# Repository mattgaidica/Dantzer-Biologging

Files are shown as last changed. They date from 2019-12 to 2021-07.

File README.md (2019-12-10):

# What is bio-logging?
The use of miniaturized, animal-borne bio-loggers to make physiological and environmental measurements from free-ranging animals is radically transforming scientific capabilities ([Williams et al., 2019](https://besjournals.onlinelibrary.wiley.com/doi/abs/10.1111/1365-2656.13094)). We have recently explored how to implement these technologies to expand the methods and resolution by which stress and performance are quantified in the wild ([Gaidica & Dantzer, 2019](https://ecoevorxiv.org/huxw6/)).

### Current Challenges
Bio-logging is historically niche due to the unique constraints of field biologists. From fish to birds, it is unreasonable to expect a one-size-fits-all solution. However, the ambitious goals of individuals *can and should* generalize to the bio-logging community under the following headings:

1. _Standardize_ data collection and analysis methods.
2. _Communicate_ approaches and insights.
3. _Innovate_ tools and technologies.

We are doing our best to make our projects **open source**. You can read more about our approach in [the Wiki](https://github.com/mattgaidica/biologging/wiki/Architecture).

## Why squirrels?
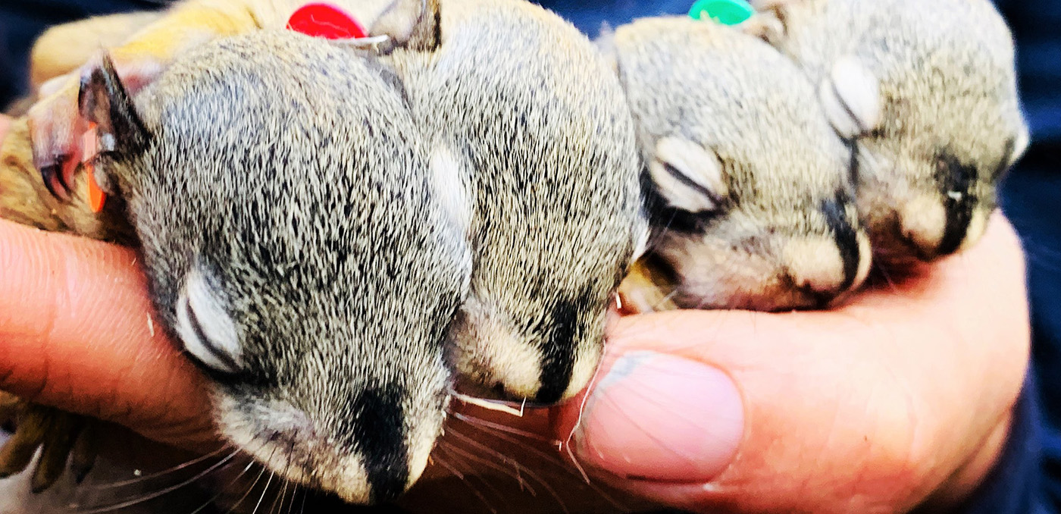
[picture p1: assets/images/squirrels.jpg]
squirrels

The ecological niche occupied by wild squirrels has been conserved for millions of years and is highlighted by their unique adaptations to arboreal life (i.e., in the trees). Their ability to regulate energy and maintain fitness through a variety of natural and imposed challenges ultimately determine their pedigree and survival. Little is known about how the central nervous system (CNS) is involved in these natural behaviors. One of our goals is to use bio-loggers to record from the CNS of wild squirrels to understand how their physiology and behavior are correlated, given the varying demands of their environment. Adding resolution to these important ecological factors is an important consideration to ongoing conservation work, potentially highlighting what ‘optimal adaptations’ are from a physiological perspective.

### Research Platform
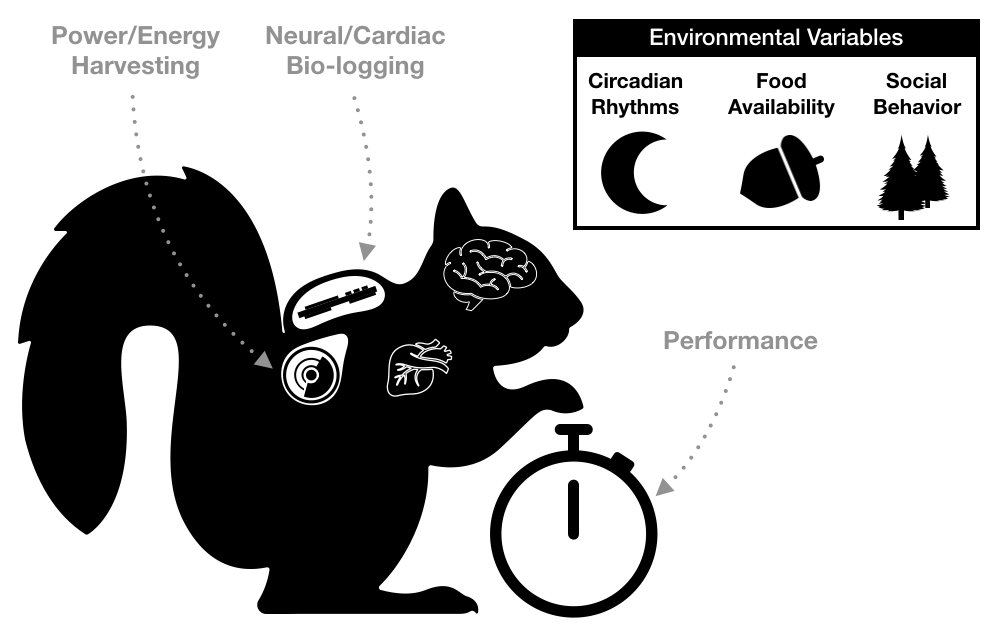
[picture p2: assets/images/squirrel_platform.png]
squirrel platform

Evolutionary pressures on wild animals engender advantageous platforms for study because behavior is so crucially linked with fitness. How mammalian physiology copes and adapts in response to changing environments is an important question that can benefit from the added resolution of bio-loggers. In addition to scientific investigations, the squirrel is a useful model to address many outstanding technical challenges—not unique to ecology—that make long-duration studies in harsh environments possible.

### Kluane Red Squirrel Project
[The Kluane Red Squirrel Project](https://redsquirrel.biology.ualberta.ca) (KRSP) is an interdisciplinary, large-scale field experiment located in the Canadian Yukon. KRSP has been collecting ecological and behavioral data on squirrels since 1987 and conducts a variety of studies and surveys on the population and food availability every year.

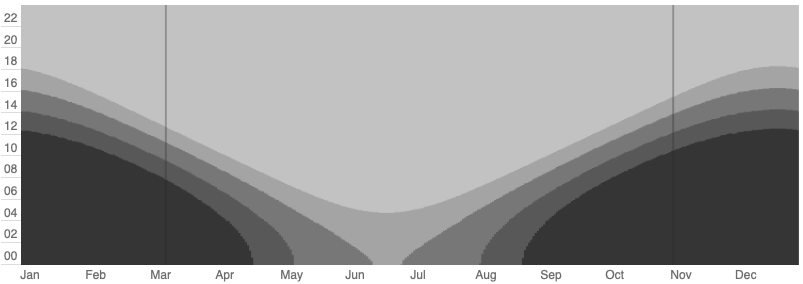
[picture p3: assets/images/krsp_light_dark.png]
whitehorse weather


Squirrels in the Yukon face intense challenges including drastic changes in light/dark cycles through each season. During the summer months there is very little darkness (see image above). This natural rhythm makes KRSP and the squirrel an ideal candidate to study the affects of circadian entrainment.

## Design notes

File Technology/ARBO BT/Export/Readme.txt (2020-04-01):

FR4, 1.6mm (0.062") thickness
1oz weight (or default/standard for copper)
Soldermask two-sided preferred, but whatever is cheapest, don't need both
4 layers
1.6mm thickness
.076mm (3mil) min trace
0.45/0.2mm through via
0.28/0.15mm blind/buried via

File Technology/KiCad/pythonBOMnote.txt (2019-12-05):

/Applications/KiCad/kicad.app/Contents/Frameworks/Python.framework/Versions/Current/bin/python "/Users/matt/Box Sync/Biologging/Technology/KiCad/KiBoM/KiBOM_CLI.py" "%I" "%O"

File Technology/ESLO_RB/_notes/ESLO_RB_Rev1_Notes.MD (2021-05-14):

SysConfig
-
* Disable DCDC (I think it does this automatically)
* Remove Axy_CS
* Change EEG_SPI to input when not used
* Remove pull-up from I2C pin instances

__Optimization__
* Build > Arm Compiler > Optimization [Optimization level -> turn on], [Floating point mode -> relaxed] will result in faster execution but may decrease precision

Hardware
-
Although you say your design seems to be operational, I’d still recommend following the CC2652RB reference design regarding the VDDS and VDDR decoupling capacitors to avoid performance issues with the RF. I also noticed that you’re missing the DCDC_SW 6.8uH inductor (L1 in the reference design). This is critical for suppressing the Switching Noise from the DC-DC Converter.

Here are some helpful links:

* SimpleLink Crystal-less BAW CC2652RB multiprotocol 2.4GHz wireless MCU dev kit (Rev. A) 
* CC13xx/CC26xx Hardware Configuration and PCB Design Considerations (Rev. E)

Alexis Rodriguez, a.rodriguez@ti.com

Additions
-
* Add UART debugging pins/test points (2 pins, RX&TX)
* Better SPI probe points for debugging

Fixes
-
__CMSIS__

* This post is not relevant, seems to be for old versions of CMSIS [E2E Forums](https://e2e.ti.com/support/microcontrollers/other/f/908/t/640978?CCS-Issues-Setting-Up-CMSIS-DSP-in-CCS#pi320995=2)
* Post on [Benchmarking FFTs](http://openaudio.blogspot.com/2016/09/benchmarking-fft-speed.html)
* [CMSIS Docs](https://docs.silabs.com/cmsis/latest/dsp/group-RealFFT#ga180d8b764d59cbb85d37a2d5f7cd9799)

1. Download CMSIS .pack from Github
2. Unpack using >> unpack200 -r -v "/Users/matt/Downloads/CMSIS.pack" "/Users/matt/Downloads/CMSIS.jar"
3. Extract .jar using The Unarchiver
4. Create static library in CCS: New project, import math files, add Include to path. *Some includes need to be copied/pasted into DSP Include (from Private Include and Core Include)*
5. Build project, link to .lib file in Debug folder from other projects.

Est. ~0.26ms for init, FFT, and findMaxBin. See also: [TI debug counter/time in CCS](http://downloads.ti.com/ccs/esd/training/workshop/ccsv7/cc13x0/site/#counter)
* Use atan2() to get angle from complex result: https://stackoverflow.com/questions/16601252/c-equivalent-of-matlab-angle-function and http://gaidi.ca/weblog/forecasting-slow-wave-activity-from-eeg-using-fft

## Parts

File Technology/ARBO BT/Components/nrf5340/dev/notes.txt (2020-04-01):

Set env variables:
>> cd /Users/matt/Documents/Software/ncs/zephyr
>> source zephyr-env.sh

>> west build -b nrf5340_dk_nrf5340_cpuapp

try setting board default?
>> west config build.board nrf5340_dk_nrf5340_cpuapp

Pristine builds:
>> west build -p auto -b nrf5340_dk_nrf5340_cpuapp samples/hello_world

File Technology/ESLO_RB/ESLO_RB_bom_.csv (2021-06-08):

Component | Description | Part | References | Value | Footprint | Quantity Per PCB | Datasheet | Digikey | Mouser
1 | Antenna | Antenna | AE1 | 2450AT42B100 | 2450AT42B100 | 1 | ~ | 712-1008-1-ND‎
2 | Unpolarized capacitor | C | C3 C11 C15 C17 C20 C22 C23 C25 C26 C27 C28 C29 | 0.1uF | C_0402_1005Metric | 12 | ~ | 490-6328-1-ND
3 | Unpolarized capacitor | C | C7 | 0.22uF | C_0402_1005Metric | 1 | ~ | 1276-1176-1-ND
4 | Unpolarized capacitor | C | C10 | 10nF | C_0402_1005Metric | 1 | ~ | 1276-1051-1-ND
5 | Unpolarized capacitor | C | C1 C2 C4 C6 | 10uF | C_0603_1608Metric | 4 | ~ | 490-14372-1-ND
6 | Unpolarized capacitor | C | C19 | 1nF | C_0402_1005Metric | 1 | ~ | 478-1101-1-ND
7 | Unpolarized capacitor | C | C5 C9 C14 C16 C18 C21 C24 | 1uF | C_0402_1005Metric | 7 | ~ | 399-4873-1-ND
8 | Unpolarized capacitor | C | C8 C12 | 2.2uF | C_0402_1005Metric | 2 | ~ | 1276-1469-1-ND
9 | Unpolarized capacitor | C | C13 | 22uF | C_0603_1608Metric | 1 | ~ | 1276-2867-1-ND
10 | 4 capacitor network, parallel topology, DIP package | C_Pack04 | CN2 CN3 | 1000pF | 0508_array | 2 | ~ | 478-W2A45C102KAT2ACT-ND
11 | 4 capacitor network, parallel topology, DIP package | C_Pack04 | CN4 CN5 | 1uF | 0508_array | 2 | ~ |  | 581-W2L16D105MAT1A
12 | 4 capacitor network, parallel topology, DIP package | C_Pack04 | CN1 | 4700pF | 0508_array | 1 | ~ |  | 581-W2A41C472KAT2A
13 | Light emitting diode | LED | D1 | LED | LED_0603_1608Metric | 1 | ~ | SML-D12V1WT86CT-ND
14 | Generic connector, single row, 01x10, script generated (kicad-library-utils/schlib/autogen/connector/) | Conn_01x10_Female | J1 | 10POS Biopotentials | ARBO_IO10_1.27mm | 1 | ~ | ED10276-ND
15 | Generic connector, single row, 01x06, script generated (kicad-library-utils/schlib/autogen/connector/) | Conn_01x06_Female | J2 | 6POS Power/JTAG | ARBO_IO6_1.27mm | 1 | ~ | ED10273-ND
16 | Inductor | L | L3 | 1.5nH | L_0402_1005Metric | 1 | ~ | 712-1411-1-ND
17 | Inductor | L | L1 | 2.2uH | L_0805_2012Metric | 1 | ~ | 490-7781-1-ND
18 | Inductor | L | L4 | 3.3nH | L_0402_1005Metric | 1 | ~ | 712-1416-1-ND
19 | Inductor | L | L2 | BLM18HE152SN1 | L_0603_1608Metric | 1 | ~ | 490-5216-1-ND
20 | Net tie, 2 pins | Net-Tie_2 | NT1 | Net-Tie_2 | NetTie-2_SMD_Pad0.5mm | 1 | ~
21 | Resistor | R | R1 R2 R3 R8 | 100k | LED_0402_1005Metric | 4 | ~ | 311-100KLRCT-ND
22 | Resistor | R | R4 | 21.5k | R_0402_1005Metric | 1 | ~ | RMCF0402FT21K5CT-ND
23 | Resistor | R | R6 R7 | 4.7k | R_0402_1005Metric | 2 | ~ | 311-4.7KJRCT-ND
24 | Resistor | R | R5 | 80.6k | R_0402_1005Metric | 1 | ~ | RMCF0402FT80K6CT-ND
25 | 4 resistor network, parallel topology, DIP package | R_Pack04 | RN3 RN4 | 1M | 0502_array | 2 | ~ | Y6105CT-ND
26 | 4 resistor network, parallel topology, DIP package | R_Pack04 | RN1 RN2 | 4.7k | 0502_array | 2 | ~ | Y6472CT-ND
27 |  | 2450BM14G0011 | U10 | 2450BM14G0011 | 2450BM14G0011 | 1 |  | 712-1620-1-ND
28 |  | ADS1294 | U9 | ADS1294 | BGA-64_8x8_8.0x8.0mm_ADS129x | 1 |  | 296-28024-1-ND
29 |  | CC2652RB | U8 | CC2652RB | QFN-48-1EP_7x7mm_P0.5mm_EP5.15x5.15mm | 1 |  | 296-CC2652RB1FRGZRCT-ND
30 | FRAM memory with SPI interface, SOIC-8 SON-8 | MB85RS2MT | U3 | CY15V104QI-20LPXC | 8-GQFN_FRAM_3.28mm-3.23mm | 1 | http://www.fujitsu.com/downloads/MICRO/fsa/pdf/products/memory/fram/MB85RS16-DS501-00014-6v0-E.pdf | 428-4724-ND
31 | 250-mA Ultra-Low-Noise Low-IQ LDO, 1.8V, SOT-23 | LP5907MFX-1.8 | U5 | LP5907MFX-1.5 | SOT-23-5 | 1 | http://www.ti.com/lit/ds/symlink/lp5907.pdf | 296-40355-1-ND
32 |  | LSM303AGR | U4 | LSM303AGR | LGA-12_2x2mm_P0.5mm | 1 |  | 497-16527-1-ND
33 |  | MAX1720 | U1 | MAX1720 | SOT-23-6 | 1 |  | MAX1720EUTGOSCT-ND
34 |  | IS37SML01G1 | U7 | MT29F2G01ABBGDWB-IT:G TR | 8x6mm_WSON_UTSO | 1 |  | 557-1665-1-ND
35 |  | TPS62740 | U2 | TPS62740 | WSON-12-1EP_3x2mm_P0.5mm_EP1x2.65 | 1 |  | 296-39459-1-ND
36 |  | TPS72325 | U6 | TPS72301DDCT | SOT-23-5 | 1 |  | 296-38438-1-ND
Component Groups: | 36
Component Count: | 65
Fitted Components: | 65
Number of PCBs: | 1
Total components: | 65
Schematic Version:
Schematic Date:
BoM Date: | Friday, June 04, 2021 at 01:24:00 PM
Schematic Source: | /Users/matt/Box Sync/Biologging/Technology/ESLO_RB/ESLO_RB.sch
KiCad Version: | Eeschema (5.1.5-0-10_14)

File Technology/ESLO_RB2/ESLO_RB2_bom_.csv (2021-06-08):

Component | Description | Part | References | Value | Footprint | Quantity Per PCB | Datasheet | Digikey | Mouser
1 | Antenna | Antenna | AE1 | 2450AT42B100 | 2450AT42B100 | 1 | ~ | 712-1008-1-ND‎
2 | Unpolarized capacitor | C | C11 C15 C17 C20 C22 C23 C25 C26 C27 C28 C29 | 0.1uF | C_0402_1005Metric | 11 | ~ | 490-6328-1-ND
3 | Unpolarized capacitor | C | C10 | 10nF | C_0402_1005Metric | 1 | ~ | 1276-1051-1-ND
4 | Unpolarized capacitor | C | C1 C2 C4 | 10uF | C_0603_1608Metric | 3 | ~ | 478-10766-2-ND
5 | Unpolarized capacitor | C | C30 C31 | 12pF | C_0402_1005Metric | 2 | ~ | 490-5924-2-ND
6 | Unpolarized capacitor | C | C19 | 1nF | C_0402_1005Metric | 1 | ~ | 478-1101-1-ND
7 | Unpolarized capacitor | C | C3 C5 C14 C16 C18 C24 | 1uF | C_0402_1005Metric | 6 | ~ | 399-4873-1-ND
8 | Unpolarized capacitor | C | C21 | 1uF | C_0603_1608Metric | 1 | ~ | 399-7847-2-ND
9 | Unpolarized capacitor | C | C7 C12 | 2.2uF | C_0402_1005Metric | 2 | ~ | 1276-1781-2-ND
10 | Unpolarized capacitor | C | C13 | 22uF | C_0603_1608Metric | 1 | ~ | 1276-1193-2-ND
11 | Unpolarized capacitor | C | C6 | 4.7uF | C_0402_1005Metric | 1 | ~ | 1276-1484-2-ND
12 | 4 capacitor network, parallel topology, DIP package | C_Pack04 | CN4 CN5 | 0.1uF | 0508_array | 2 | ~ | 478-7584-2-ND
13 | 4 capacitor network, parallel topology, DIP package | C_Pack04 | CN2 CN3 | 1000pF | 0508_array | 2 | ~ | 478-13177-2-ND
14 | 4 capacitor network, parallel topology, DIP package | C_Pack04 | CN1 | 4700pF | 0612_array | 1 | ~ | 399-CA064X473K4RACTUTR-ND
15 | Light emitting diode | LED | D1 D2 | LED | LED_0402_1005Metric | 2 | ~ | VLMB1500-GS08CT-ND VLMO1500-GS08CT-ND
16 | Ferrite bead | Ferrite_Bead | FB1 | Ferrite_Bead | C_0603_1608Metric | 1 | ~ | 490-5216-2-ND
17 | Generic connector, single row, 01x08, script generated (kicad-library-utils/schlib/autogen/connector/) | Conn_01x08_Female | J1 J2 | Biopotentials | ESLO_IO_8_1-27 | 2 | ~ | ED8250-ND ED90570-ND
18 | Generic connector, single row, 01x02, script generated (kicad-library-utils/schlib/autogen/connector/) | Conn_01x02_Female | J3 | Conn_01x02_Female | ESLO_2pin_THERM | 1 | ~
19 | Inductor | L | L3 | 1.5nH | L_0402_1005Metric | 1 | ~ | 334-1083-2-ND
20 | Inductor | L | L1 | 2.2uH | L_0805_2012Metric | 1 | ~ | 490-4994-2-ND
21 | Inductor | L | L4 | 3.3nH | L_0402_1005Metric | 1 | ~ | 712-1416-1-ND
22 | Net tie, 2 pins | Net-Tie_2 | NT1 | Net-Tie_2 | NetTie-2_SMD_Pad0.5mm | 1 | ~
23 | Resistor | R | R1 R2 R3 R8 | 100k | LED_0402_1005Metric | 4 | ~ | 311-100KLRCT-ND
24 | Resistor | R | R4 | 21.5k | R_0402_1005Metric | 1 | ~ | RMCF0402FT21K5CT-ND
25 | Resistor | R | R5 | 80.6k | R_0402_1005Metric | 1 | ~ | RMCF0402FT80K6CT-ND
26 | 4 resistor network, parallel topology, DIP package | R_Pack04 | RN3 RN4 | 1M | 0502_array | 2 | ~ | Y6105CT-ND
27 | 4 resistor network, parallel topology, DIP package | R_Pack04 | RN1 RN2 | 4.7k | 0502_array | 2 | ~ | Y6472CT-ND
28 |  | 2450BM14G0011 | U10 | 2450BM14G0011 | 2450BM14G0011 | 1 |  | 712-1620-1-ND
29 |  | ADS1294 | U9 | ADS1294 | BGA-64_8x8_8.0x8.0mm_ADS129x | 1 |  | 296-28024-1-ND
30 |  | IS37SML01G1 | U7 | AS5F18G04SND-10LIN | 8x6mm_WSON_UTSO | 1 |  | 1450-AS5F18G04SND-10LIN-ND | 340-319932-REEL
31 |  | CC2652RB | U8 | CC2652R1FRGZT | QFN-48-1EP_7x7mm_P0.5mm_EP5.15x5.15mm | 1 |  |  | 595-CC2652R1FRGZR
32 | I2C/SPI, iNEMO inertial module: always-on 3D accelerometer and 3D gyroscope | LSM6DS3 | U3 | LSM6DSOXTR | LGA-14_3x2.5mm_P0.5mm_LayoutBorder3x4y | 1 | www.st.com/resource/en/datasheet/lsm6ds3.pdf | 497-18367-2-ND
33 |  | MAX1720 | U1 | MAX1720 | SOT-23-6 | 1 |  | MAX1720EUTGOSCT-ND
34 |  | TPS62243_WSON | U4 | TPS62243_WSON | WSON-6-1EP_2x2mm_P0.65mm_EP1x1.6mm | 1 |  | 296-46476-1-ND
35 |  | TPS723_WSON | U6 | TPS72301DRVR | WSON-6-1EP_2x2mm_P0.65mm_EP1x1.6mm | 1 |  | 296-TPS72301DRVRTR-ND
36 |  | TPS7A20_X2SON | U2 | TPS7A2015PDQNR | Texas_X2SON-4_1x1mm_P0.65mm | 1 |  | 296-TPS7A2015PDQNRTR-ND
37 | Two pin crystal | Crystal | Y2 | 32.768kHz | Crystal_SMD_2012-2Pin_2.0x1.2mm | 1 | ~ | SER4081TR-ND
38 | Four pin crystal, GND on pins 2 and 4 | Crystal_GND24 | Y1 | 48MHz | Crystal_SMD_2016-4Pin_2.0x1.6mm | 1 | ~ | 535-13927-2-ND
Component Groups: | 38
Component Count: | 66
Fitted Components: | 66
Number of PCBs: | 1
Total components: | 66
Schematic Version:
Schematic Date:
BoM Date: | Tuesday, June 01, 2021 at 11:29:35 AM
Schematic Source: | /Users/matt/Box Sync/Biologging/Technology/ESLO_RB2/ESLO_RB2.sch
KiCad Version: | Eeschema (5.1.5-0-10_14)

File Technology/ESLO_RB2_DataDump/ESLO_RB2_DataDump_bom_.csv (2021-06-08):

Component | Description | Part | References | Value | Footprint | Quantity Per PCB | Datasheet | Digikey
1 | Unpolarized capacitor | C | C2 | 10uF | C_0603_1608Metric | 1 | ~ | 478-8050-1-ND
2 | Generic connector, single row, 01x08, script generated (kicad-library-utils/schlib/autogen/connector/) | Conn_01x08_Female | J1 | Conn_01x08_Female | 8pin_1-27pitch_SMD | 1 | ~ | ED90570-ND
3 | Capacitor symbol for simulation only | INDUCTOR | L1 | 2.2uH | L_0805_2012Metric | 1 | ~ | 490-4994-1-ND
4 | Resistor | R | R1 R2 | 10k | R_0603_1608Metric | 2 | ~ | CR0603-JW-103ELFCT-ND
5 | Resistor | R | R3 R4 | 8.25k | R_0603_1608Metric | 2 | ~ | RMCF0603FT8K25CT-ND
6 | Double Pole Single Throw (DPST) Switch | SW_DPST | SW1 | SW_DPST | SW_SPST_TL3305A | 1 | ~ | EG5353CT-ND
7 |  | Adalogger | U2 | Adalogger | Adafruit_feather | 1 |  | 1528-1539-ND
8 |  | SN74ACX1T45 | U3 U4 | SN74ACX1T45 | SOT-363_SC-70-6 | 2 |  | 296-SN74AXC1T45QDCKRQ1CT-ND
9 |  | TPS62243_WSON | U1 | TPS62243_WSON | WSON-6-1EP_2x2mm_P0.65mm_EP1x1.6mm | 1 |  | TPS62243DRVR
Component Groups: | 9
Component Count: | 12
Fitted Components: | 12
Number of PCBs: | 1
Total components: | 12
Schematic Version:
Schematic Date:
BoM Date: | Wednesday, June 02, 2021 at 09:34:16 AM
Schematic Source: | /Users/matt/Box Sync/Biologging/Technology/ESLO_RB2_DataDump/ESLO_RB2_DataDump.sch
KiCad Version: | Eeschema (5.1.5-0-10_14)

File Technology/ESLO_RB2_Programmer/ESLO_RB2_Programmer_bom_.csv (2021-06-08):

Component | Description | Part | References | Value | Footprint | Quantity Per PCB | Datasheet | Digikey
1 | Unpolarized capacitor | C | C1 | 10uF | C_0603_1608Metric | 1 | ~ | 478-8050-1-ND‎
2 | Light emitting diode | LED | D1 | LED | D_0603_1608Metric | 1 | ~ | 475-3442-1-ND
3 | Generic connector, single row, 01x08, script generated (kicad-library-utils/schlib/autogen/connector/) | Conn_01x08_Female | J3 | Conn_01x08_Female | 8pin_1-27pitch_SMD | 1 | ~ | ED90570-ND
4 | Generic connector, single row, 01x03, script generated (kicad-library-utils/schlib/autogen/connector/) | Conn_01x03_Male | J1 | LP-P10 | PinHeader_1x03_P2.54mm_Vertical | 1 | conn-SAM8930-ND | A19430-ND
5 | Cortex Debug Connector, standard ARM Cortex-M SWD and JTAG interface | Conn_ARM_JTAG_SWD_10 | J2 | LP-P7 | PinHeader_2x05_P1.27mm_Vertical_SMD | 1 | http://infocenter.arm.com/help/topic/com.arm.doc.ddi0314h/DDI0314H_coresight_components_trm.pdf | SAM13165CT-ND
6 | Capacitor symbol for simulation only | INDUCTOR | L1 | 2.2uH | R_0805_2012Metric | 1 | ~ | 490-4994-1-ND‎
7 | Switch, single pole double throw | SW_SPDT | SW1 | SW_SPDT | PinSocket_1x03_P2.54mm_Vertical | 1 | ~ | 360-2133-ND
8 |  | TPS62243_WSON | U1 | TPS62243_WSON | WSON-6-1EP_2x2mm_P0.65mm_EP1x1.6mm | 1 |  | 296-46476-1-ND‎
Component Groups: | 8
Component Count: | 8
Fitted Components: | 8
Number of PCBs: | 1
Total components: | 8
Schematic Version:
Schematic Date:
BoM Date: | Wednesday, June 02, 2021 at 09:28:16 AM
Schematic Source: | /Users/matt/Box Sync/Biologging/Technology/ESLO_RB2_Programmer/ESLO_RB2_Programmer.sch
KiCad Version: | Eeschema (5.1.5-0-10_14)

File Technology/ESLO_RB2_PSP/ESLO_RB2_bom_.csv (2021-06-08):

Component | Description | Part | References | Value | Footprint | Quantity Per PCB | Datasheet | Digikey | Mouser
1 | Antenna | Antenna | AE1 | 2450AT42B100 | 2450AT42B100 | 1 | ~ | 712-1008-1-ND‎
2 | Unpolarized capacitor | C | C11 C17 C20 C22 C23 C25 C26 C28 C29 | 0.1uF | C_0402_1005Metric | 9 | ~ | 490-6328-1-ND
3 | Unpolarized capacitor | C | C10 | 10nF | C_0402_1005Metric | 1 | ~ | 1276-1051-1-ND
4 | Unpolarized capacitor | C | C2 C4 | 10uF | C_0603_1608Metric | 2 | ~ | 478-10766-2-ND
5 | Unpolarized capacitor | C | C30 C31 | 12pF | C_0402_1005Metric | 2 | ~ | 490-5924-2-ND
6 | Unpolarized capacitor | C | C3 C5 C21 | 1uF | C_0402_1005Metric | 3 | ~ | 399-4873-1-ND
7 | Unpolarized capacitor | C | C1 C12 | 2.2uF | C_0402_1005Metric | 2 | ~ | GRM155R61E225KE11D
8 | Unpolarized capacitor | C | C6 | 4.7uF | C_0402_1005Metric | 1 | ~ | 1276-1484-2-ND
9 | Light emitting diode | LED | D1 D2 | LED | LED_0603_1608Metric | 2 | ~ | SML-D12V1WT86CT-ND
10 | Generic connector, single row, 01x08, script generated (kicad-library-utils/schlib/autogen/connector/) | Conn_01x08_Female | J1 J2 | Biopotentials | ESLO_IO_8_1-27 | 2 | ~ | ED8250-ND ED90570-ND
11 | Generic connector, single row, 01x02, script generated (kicad-library-utils/schlib/autogen/connector/) | Conn_01x02_Female | J3 | Conn_01x02_Female | ESLO_2pin_THERM | 1 | ~
12 | Inductor | L | L3 | 1.5nH | L_0402_1005Metric | 1 | ~ | 334-1083-2-ND
13 | Inductor | L | L1 | 2.2uH | L_0805_2012Metric | 1 | ~ | 490-4994-2-ND
14 | Inductor | L | L4 | 3.3nH | L_0402_1005Metric | 1 | ~ | 712-1416-1-ND
15 | Net tie, 2 pins | Net-Tie_2 | NT1 | Net-Tie_2 | NetTie-2_SMD_Pad0.5mm | 1 | ~
16 | Resistor | R | R1 R2 R3 R8 | 100k | LED_0402_1005Metric | 4 | ~ | 311-100KLRCT-ND
17 | Resistor | R | R4 | 21.5k | R_0402_1005Metric | 1 | ~ | RMCF0402FT21K5CT-ND
18 | Resistor | R | R5 | 80.6k | R_0402_1005Metric | 1 | ~ | RMCF0402FT80K6CT-ND
19 |  | 2450BM14G0011 | U10 | 2450BM14G0011 | 2450BM14G0011 | 1 |  | 712-1620-1-ND
20 |  | IS37SML01G1 | U7 | AS5F18G04SND-10LIN | 8x6mm_WSON_UTSO | 1 |  | 1450-AS5F34G04SND-08LIN-ND | 340-319932-REEL
21 |  | CC2652RB | U8 | CC2652R1FRGZT | QFN-48-1EP_7x7mm_P0.5mm_EP5.15x5.15mm | 1 |  |  | 595-CC2652R1FRGZR
22 | I2C/SPI, iNEMO inertial module: always-on 3D accelerometer and 3D gyroscope | LSM6DS3 | U3 | LSM6DSOXTR | LGA-14_3x2.5mm_P0.5mm_LayoutBorder3x4y | 1 | www.st.com/resource/en/datasheet/lsm6ds3.pdf | 497-18367-2-ND
23 |  | MAX1720 | U1 | MAX1720 | SOT-23-6 | 1 |  | MAX1720EUTGOSCT-ND
24 |  | TPS6223xx | U4 | TPS6223xx | USON6-1.45x1.00mm-0.5pads | 1 |  | 296-39453-2-ND
25 |  | TPS72325 | U6 | TPS72301DRVR | WSON-6-1EP_2x2mm_P0.65mm_EP1x1.6mm | 1 |  | 296-TPS72301DRVRTR-ND
26 |  | TPS7A20_X2SON | U2 | TPS7A2015PDQNR | Texas_X2SON-4_1x1mm_P0.65mm | 1 |  | 296-TPS7A2015PDQNRTR-ND
27 | Two pin crystal | Crystal | Y2 | 32.768kHz | Crystal_SMD_2012-2Pin_2.0x1.2mm | 1 | ~ | SER4081TR-ND
28 | Four pin crystal, GND on pins 2 and 4 | Crystal_GND24 | Y1 | 48MHz | Crystal_SMD_2016-4Pin_2.0x1.6mm | 1 | ~ | 535-13927-2-ND
Component Groups: | 28
Component Count: | 46
Fitted Components: | 46
Number of PCBs: | 1
Total components: | 46
Schematic Version:
Schematic Date:
BoM Date: | Monday, May 03, 2021 at 05:46:10 PM
Schematic Source: | /Users/matt/Box Sync/Biologging/Technology/ESLO_RB2_PSP/ESLO_RB2.sch
KiCad Version: | Eeschema (5.1.5-0-10_14)

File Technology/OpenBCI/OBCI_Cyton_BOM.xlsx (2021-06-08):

 | OBCI_V3_C
Item | Board Ref | Qty | Component | Value | Package | Manufacturer | Part Number | Description | Notes
1 | C2,C4 | 2 | C | 100uF | SM 1206 | Yageo | CC1206MKX5R5BB107 | MLCC
2 | C1,C8,C25,C29,C31,C33,C37 | 7 | C | 10uF | SM0603 | Murata | GRM188C80G106KE47D | MLCC
3 | C32,C35,C36,C38,C40 | 5 | C | 2.2uF | EIA_0402 | Murata | GRM155C80J225ME95D | MLCC
4 | C39 | 1 | C | 2.2uF | EIA_0402 | Murata | GRM155R61C225KE44D | MLCC
5 | C6,C7,C14,C17,C18,C19,C21,C22,C27 | 9 | C | 1uF | EIA_0402 | Yageo | CC0402KRX7R5BB105 | MLCC
6 | C5,C10,C12,C13,C15,C24,C28 | 7 | C | 0.1uF | EIA_0402 | Yageo | CC0402KRX7R7BB104 | MLCC
7 | C30 | 1 | C | 0.01uF | EIA_0402 | Yageo | CC0402KRX7R7BB103 | MLCC
8 | C16 | 1 | C | 0.001uF | EIA_0402 | Yageo | CC0402KRX7R7BB102 | MLCC
9 | C20,C23 | 2 | C | 18pF | EIA_0402 | Yageo | CC0402JRNPO9BN180 | MLCC
10 | R1,R2,R3,R4,R6 | 5 | R | 2.2K | SM | BOURNS | CAY16-2201F4LF | 4 R-ARRAY
11 | C3,C9,C11,C26,C34 | 5 | C | 0.001uF | SM | TDK | CKCL44X7R1H102M085AA | 4 CAP ARRAY
12 | U1 | 1 | U |  | LGA | ST | LIS3DHTR | ST ACCELEROMETER
13 | U2 | 1 | U |  | SM | TI | SN74LVC1G32DCKR | OR_GATE
14 | U3 | 1 | U |  | SOT-23-6 | TI | LM2664M6/NOPB | V INVERTER
15 | U4 | 1 | U |  | SOT-23-5 | TI | TLV70025QDDCRQ1 | +2.5V LDO REG
16 | U5 | 1 | U |  | SM | Microchip | MCP1754T-3302E/OT | 3V3 LDO REG
17 | U6 | 1 | U |  | TQFP-64 | TI | ADS1299IPAG | ADS1299 | Consigned by OpenBCI, Inc
18 | U7 | 1 | U |  | SSOP-28 | Microchip | PIC32MX250F128B-I/SS | PIC32 MICROCONTROLLER
19 | VR1 | 1 | VR |  | SM | TI | TPS72325DBVR | -2.5 LDO REG
20 | BLE1 | 1 | BLE |  | SM | RF DIGITAL | RFD22301 | BTLE Module | Consigned by OpenBCI, Inc
21 | D1 | 1 | D | LED | SM 0603 | Lite-On | LTST-C193TBKT-5A | BLUE LED
22 | D8 | 2 | D |  | SM 0603 | Comchip | CDSU400B | DIODE
23 | D9 | 1 | D |  | SM 0603 | Comchip | CDBU0130L | DIODE
24 | D2,D3,D4,D5,D6,D7 | 6 | D |  | SM | TI | TPD4E1B06DCKR | TI QUAD TVS
25 | D10 | 1 | D | 3V | SOD-923 | Comchip | CZRQR52C3-HF | 3V Zener Diode
26 | R8,R10,R11 | 3 | R | 1K | EIA_0402 | Yageo | RT0402FRE071KL | Resistor
27 | R5 | 1 | R | 1M | EIA_0402 | Yageo | RC0402JR-071ML | Resistor
28 | R7,R9 | 2 | R | 470K | EIA_0402 | Yageo | RC0402JR-07470KL | Resistor
29 | X1 | 1 | X | 8MHz | SM | ABRACON | ABMM2-8.000MHZ-E2-T | 8MHz XTAL
30 | B1 | 1 | BATT |  | SM | JST Sales | S2B-PH-SM4-TB(LF)(SN) | CONN HEADER PH SIDE 2POS 2MM SMD
31 | SW2 | 1 | S |  | SM | COPAL | CUS-13TB | SP3T SLIDE SWITCH
32 | SW1,SW3 | 2 | S |  | SM | C&K | PTS810 SJK 250 SMTR LFS | TACT SWITCH
33 | CONN1 | 1 | CONN |  | SM |  |  | microSD card slot | Consigned by OpenBCI, Inc
34 | PL1 | 1 | J |  | DIP | Wurth | 61302221021 | Dual 11 x 2 0.1" pitch MALE header row Right Angle

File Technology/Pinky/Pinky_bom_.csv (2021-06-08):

Component | Description | Part | References | Value | Footprint | Quantity Per PCB | Datasheet | Digikey
1 | Antenna | Antenna | AE1 AE2 | Antenna | Linx_Ant_Screw | 2 | ~ | ANT-315-PW-LP-ND
2 | Unpolarized capacitor | C | C7 | .039uF | C_0603_1608Metric | 1 | ~ | 311-4072-1-ND
3 | Unpolarized capacitor | C | C6 | 1.8pF | C_0603_1608Metric | 1 | ~ | 490-9667-2-ND
4 | Unpolarized capacitor | C | C3 C5 | 15pF | C_0402_1005Metric | 2 | ~ | 399-8947-1-ND
5 | Unpolarized capacitor | C | C9 | 1uF | C_0603_1608Metric | 1 | ~ | 1276-1182-1-ND
6 | Unpolarized capacitor | C | C8 C10 | 2.2uF | C_0603_1608Metric | 2 | ~ | 399-7886-1-ND
7 | Unpolarized capacitor | C | C2 | 220pF | C_0402_1005Metric | 1 | ~ | 490-6220-1-ND
8 | Unpolarized capacitor | C | C4 | 22pF | C_0402_1005Metric | 1 | ~ | 490-5868-1-ND
9 | Unpolarized capacitor | C | C1 | 680pF | C_0402_1005Metric | 1 | ~ | 399-1027-1-ND
10 | Light emitting diode | LED | D1 | +3.3V | D_0603_1608Metric | 1 | ~ | 732-4971-1-ND
11 | Light emitting diode | LED | D2 | +5V | D_0603_1608Metric | 1 | ~ | 732-4971-1-ND
12 | Light emitting diode | LED | D4 | +6V | D_0603_1608Metric | 1 | ~ | 732-4971-1-ND
13 | Light emitting diode | LED | D3 | -6V | D_0603_1608Metric | 1 | ~ | 732-4971-1-ND
14 | Light emitting diode | LED | D5 | PINK_EN | D_0603_1608Metric | 1 | ~ | 732-4978-1-ND
15 | Generic connector, single row, 01x02, script generated (kicad-library-utils/schlib/autogen/connector/) | Conn_01x02_Female | J4 | SPEAKER | TerminalBlock_4Ucon_1x02_P3.50mm_Horizontal | 1 | ~ | 277-1860-ND
16 | Generic screw terminal, single row, 01x04, script generated (kicad-library-utils/schlib/autogen/connector/) | Screw_Terminal_01x04 | J2 J3 | SPI CONN | TerminalBlock_4Ucon_1x04_P3.50mm_Horizontal | 2 | ~ | 277-1860-ND
17 | Generic connector, single row, 01x04, script generated (kicad-library-utils/schlib/autogen/connector/) | Conn_01x04_Male | J1 | TX CONN | PinHeader_1x04_P2.54mm_Vertical | 1 | ~
18 | Inductor | L | L1 | 22nH | L_0402_1005Metric | 1 | ~ | 712-1455-1-ND
19 | Inductor | L | L2 | 27nH | L_0402_1005Metric | 1 | ~ | 712-1413-1-ND
20 | Capacitor symbol for simulation only | INDUCTOR | L3 | 56nH | L_0603_1608Metric | 1 | ~ | 712-1443-1-ND
21 | Resistor | R | R1 | 0 | R_0402_1005Metric | 1 | ~ | 1276-3480-1-ND
22 | Resistor | R | R2 R3 R4 R6 R8 | 2.2k | R_0603_1608Metric | 5 | ~ | P2.2KGCT-ND
23 | Resistor | R | R5 R7 | 4.7k | R_0603_1608Metric | 2 | ~ | RR08P4.7KDCT-ND
24 | Potentiometer | R_POT | RV1 | 5k | Potentiometer_Bourns_3314J_Vertical | 1 | ~ | ST4ETA502CT-ND
25 | 150mA low dropout linear regulator, wide input voltage range, 5.0V fixed positive output, SOT-23-5 package | AP2204K-5.0 | U7 | AP2204K-5.0 | SOT-23-5 | 1 | https://www.diodes.com/assets/Datasheets/AP2204.pdf | AP2204K-5.0TRG1DICT-ND
26 |  | Adalogger | U4 | Adalogger | Adafruit_feather | 1 |  | 1528-1539-ND
27 |  | MAX1472 | U1 | MAX1472 | SOT-23-8 | 1 |  | MAX1472AKA+TCT-ND
28 | Microchip Technology Digital Temperature Sensor MSOP | MCP9804_MSOP | U3 | MCP9808_MSOP | MSOP-8_3x3mm_P0.65mm | 1 | http://ww1.microchip.com/downloads/en/DeviceDoc/22203b.pdf | MCP9808T-E/MSCT-ND
29 |  | MICRF007 | U2 | MICRF007 | SOIC-8_3.9x4.9mm_P1.27mm | 1 |  | 576-1334-ND
30 |  | NOISE2 | U6 | NOISE2 | DIP-8_W7.62mm | 1 |  | AE9986-ND
31 |  | SN74LVC | U8 | SN74LVC | SOT-353_SC-70-5 | 1 |  | 296-13254-1-ND
32 | Single Low-Noise JFET-Input Operational Amplifiers, DIP-8/SOIC-8 | TL071 | U9 | TL071 | SOIC-8_3.9x4.9mm_P1.27mm | 1 | http://www.ti.com/lit/ds/symlink/tl071.pdf | 296-14994-1-ND
33 |  | VEML7700 | U5 | VEML7700 | VEML7700 | 1 |  | VEML7700CT-ND
34 | Two pin crystal | Crystal | Y2 | 4.8970MHz | Crystal_SMD_HC49-SD | 1 | ~ | 535-9688-1-ND
35 | Two pin crystal | Crystal | Y1 | 9.84375MHz | Crystal_SMD_Abracon_ABM3-2Pin_5.0x3.2mm | 1 | ~ | 535-13417-1-ND
Component Groups: | 35
Component Count: | 44
Fitted Components: | 44
Number of PCBs: | 1
Total components: | 44
Schematic Version:
Schematic Date:
BoM Date: | Tuesday, June 30, 2020 at 06:02:59 PM
Schematic Source: | /Users/matt/Box Sync/Biologging/Technology/Pinky/Pinky.sch
KiCad Version: | Eeschema (5.1.5-0-10_14)

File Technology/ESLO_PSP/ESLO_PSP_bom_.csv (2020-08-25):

Component | Description | Part | References | Value | Footprint | Quantity Per PCB | Datasheet | Digikey
1 | Single-cell battery | Battery_Cell | BT1 | Coin Cell | BatteryHolder_Keystone_1058_1x2032 | 1 | ~ | 36-1058-ND
2 | Unpolarized capacitor | C | C13 | 1.5pF | C_0402_1005Metric | 1 | ~ | 490-6212-2-ND
3 | Unpolarized capacitor | C | C8 C9 | 10nF | C_0402_1005Metric | 2 | ~ | 490-6326-2-ND
4 | Unpolarized capacitor | C | C10 | 1nF | C_0402_1005Metric | 1 | ~ | 490-6350-2-ND
5 | Unpolarized capacitor | C | C14 | 1pF | C_0402_1005Metric | 1 | ~ | 490-6206-2-ND
6 | Unpolarized capacitor | C | C1 C2 C3 C4 C5 | 1uF | C_0402_1005Metric | 5 | ~ | 399-4873-1-ND
7 | Unpolarized capacitor | C | C12 | 2.2nF | C_0402_1005Metric | 1 | ~ | 311-1037-1-ND
8 | Unpolarized capacitor | C | C6 C7 | 2.2uF | C_0402_1005Metric | 2 | ~ | 490-10451-1-ND
9 | Unpolarized capacitor | C | C16 C17 | 22pF | C_0402_1005Metric | 2 | ~ | 311-1652-1-ND
10 | Unpolarized capacitor | C | C15 | 33nF | C_0402_1005Metric | 1 | ~ | 490-11984-2-ND
11 | Unpolarized capacitor | C | C11 | 4.7pF | C_0402_1005Metric | 1 | ~ | 490-5874-2-ND
12 | Generic screw terminal, single row, 01x02, script generated (kicad-library-utils/schlib/autogen/connector/) | Screw_Terminal_01x02 | J1 | Imeas | TerminalBlock_4Ucon_1x02_P3.50mm_Horizontal | 1 | ~
13 | Jumper, normally closed | Jumper | JP1 | Jumper | PinHeader_1x02_P2.54mm_Vertical | 1 | ~ | S9337-ND
14 | Inductor | L | L1 | 2.7nH | L_0402_1005Metric | 1 | ~ | 2035-0402HP-2N7EJTSCT-ND
15 | Inductor | L | L3 | 3.9nH | L_0402_1005Metric | 1 | ~ | 2035-0402HS-3N9EGTSCT-ND
16 | Inductor | L | L2 | 8.2nH | L_0402_1005Metric | 1 | ~ | 2035-1500-1-ND
17 | Net tie, 2 pins | Net-Tie_2 | NT1 | Net-Tie_2 | SolderJumper-2_P1.3mm_Bridged2Bar_Pad1.0x1.5mm | 1 | ~
18 | Generic connector, single row, 01x15, script generated (kicad-library-utils/schlib/autogen/connector/) | Conn_01x15 | P5 P6 | Digital | Socket_Strip_Arduino_1x15 | 2 |  | S7013-ND
19 | Resistor | R | R1 | 10k | R_0402_1005Metric | 1 | ~ | 311-10.0KLRCT-ND
20 | Resistor | R | R4 | 22k | R_0402_1005Metric | 1 | ~ | 311-22.0KLRCT-ND
21 | Resistor | R | R2 | 33k | R_0402_1005Metric | 1 | ~ | P33KDCCT-ND
22 | Resistor | R | R3 | 63.4k | R_0402_1005Metric | 1 | ~ | YAG3204CT-ND
23 |  | AN91445_MG | U6 | AN91445 | AN91445_MG | 1
24 | 250-mA Ultra-Low-Noise Low-IQ LDO, 1.5V, SOT-23 | LP5907MFX-1.5 | U2 | LP5907MFX-1.5 | SOT-23-5 | 1 | http://www.ti.com/lit/ds/symlink/lp5907.pdf | 296-40355-1-ND
25 | 250-mA Ultra-Low-Noise Low-IQ LDO, 1.8V, SOT-23 | LP5907MFX-1.8 | U1 | LP5907MFX-1.8 | SOT-23-5 | 1 | http://www.ti.com/lit/ds/symlink/lp5907.pdf | 296-41463-1-ND
26 |  | MAX1720 | U3 | MAX1720 | SOT-23-6 | 1 |  | MAX1720EUTGOSCT-ND
27 |  | TPS72325 | U4 | TPS72301DDCT | SOT-23-5 | 1 |  | 296-38438-1-ND
28 | nRF24L01+, Ultra low power 2.4GHz RF Transceiver, QFN20 4x4mm | nRF24L01P | U5 | nRF24L01P | QFN-20-1EP_4x4mm_P0.5mm_EP2.5x2.5mm | 1 | http://www.nordicsemi.com/eng/content/download/2726/34069/file/nRF24L01P_Product_Specification_1_0.pdf | 1490-1033-1-ND
29 | Four pin crystal, GND on pins 2 and 4, small symbol | Crystal_GND24_Small | Y1 | SXT21412AA16 | SXT214 | 1 | ~ | 2388-SXT21412AA16-16.000M-ND
Component Groups: | 29
Component Count: | 37
Fitted Components: | 37
Number of PCBs: | 1
Total components: | 37
Schematic Version:
Schematic Date: | jeu. 02 avril 2015
BoM Date: | Thursday, August 20, 2020 at 12:32:59 PM
Schematic Source: | /Users/matt/Box Sync/Biologging/Technology/ESLO_PSP/ESLO_PSP.sch
KiCad Version: | Eeschema (5.1.5-0-10_14)

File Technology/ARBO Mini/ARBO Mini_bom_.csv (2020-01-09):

Component | Description | Part | References | Value | Footprint | Quantity Per PCB | Datasheet | Manufacturer Part Number | Digi-key Part Number | Link
1 | Unpolarized capacitor | C | C11 C15 C18 C19 C22 C32 C35 | 0.1uF | C_0402_1005Metric | 7 | ~ | LMK105BJ104KV-F | 587-1227-1-ND
2 | Unpolarized capacitor | C | C13 C14 C20 C21 C25 C26 C27 C29 C30 C38 | 1000pF | C_0402_1005Metric | 10 | ~ | GRM1555C1H102JA01J | 490-6190-1-ND
3 | Unpolarized capacitor | C | C5 C6 C7 C23 | 10uF | C_0603_1608Metric | 4 | ~ | GRM155R60E106ME16D | 490-10692-1-ND
4 | Unpolarized capacitor | C | C1 C8 C16 C31 C34 C36 C37 | 1uF | C_0402_1005Metric | 7 | ~ | C0402C105K9PACTU | 399-4873-1-ND
5 | Unpolarized capacitor | C | C2 C3 | 22pF | C_0402_1005Metric | 2 | ~ | C0402C105K9PACTU | 399-4873-1-ND
6 | Unpolarized capacitor | C | C33 | 22uF | C_0603_1608Metric | 1 | ~ | GRM188R60J226MEA0D | 490-7611-1-ND
7 | Polarized capacitor, US symbol | CP1 | C4 C9 C10 | 3.3uF | C_0402_1005Metric | 3 | ~ | C1005X5R0G335K050BB | 445-5948-1-ND
8 | Unpolarized capacitor | C | C12 C17 C24 C28 | 4.7nF | C_0402_1005Metric | 4 | ~ | C0402C472K4RECAUTO | 399-17875-1-ND
9 |  | JST-PH | CONN1 | JST-PH | PinHeader_1x02_P2.00mm_Horizontal | 1
10 | Light emitting diode | LED | D5 | GRN | LED_0402_1005Metric | 1 | ~ | 150040VS73240 | 732-11992-1-ND
11 | Schottky diode | D_Schottky | D1 | MBR120 | D_SOD-123F | 1 | https://www.digikey.com/product-detail/en/on-semiconductor/MBR120VLSFT1G/MBR120VLSFT1GOSCT-ND/893874 | MBR120VLSFT1G | MBR120VLSFT1GOSCT-ND
12 | Light emitting diode | LED | D3 D4 | RED | LED_0402_1005Metric | 2 | ~ | 150040RS73240 | 732-11991-1-ND
13 | Generic connector, single row, 01x12, script generated (kicad-library-utils/schlib/autogen/connector/) | Conn_01x12 | J3 | Conn_01x10 | Hirose_DF52-12S-0.8H_1x12-1MP_P0.80mm_Horizontal | 1 | ~ | DF52-12S-0.8H(21) | H125103CT-ND
14 | Micro SD Card Socket with card detection pins | Micro_SD_Card_473093351 | J2 | Micro_SD_Card_473093351 | 473093351_uSDCard | 1 | https://www.hirose.com/product/en/download_file/key_name/DM3/category/Catalog/doc_file_id/49662/?file_category_id=4&item_id=195&is_series=1 | 0473093351 | WM10795CT-ND
15 | USB Micro Type B connector | USB_B_Micro | J1 | USB_B_Micro | USB_Micro-B_Molex-105017-0001 | 1 | ~ | 1050170001 | WM1399CT-ND
16 | Resistor | R | R6 | 0 | R_0402_1005Metric | 1 | ~ | RC0402JR-070RL | 311-0.0JRCT-ND
17 | Resistor | R | R1 R5 | 100K | R_0402_1005Metric | 2 | ~ | RC0402FR-07100KL | 311-100KLRCT-ND
18 | Resistor | R | R3 R4 R8 | 10K | R_0402_1005Metric | 3 | ~ | RC0402FR-0710KL | 311-10.0KLRCT-ND
19 | Resistor | R | R16 | 1M | R_0402_1005Metric | 1 | ~ | RC0402FR-071ML | 311-1.00MLRCT-ND
20 | Resistor | R | R2 R7 R9 R10 R11 R12 R13 R14 R15 R17 R18 | 2.2K | R_0402_1005Metric | 11 | ~ | RC0402FR-072K2L | 311-2.20KLRCT-ND
21 | Single Pole Single Throw (SPST) switch | SW_SPST | SW1 | SW_SPST | SW_SPST_CK_KXT3 | 1 | ~ | KXT 331 LHS | CKN10779CT-ND
22 |  | ADS1294_TQFP | U7 | ADS1294 | TQFP-64-1EP_10x10mm_P0.5mm_EP8x8mm | 1 |  | ADS1294IPAG | 296-27932-ND
23 | SAM D21 Microchip SMART ARM-based Flash MCU, 48Mhz, 256K Flash, 32K SRAM, TQFP-48 | ATSAMD21G18A-AUT | U6 | ATSAMD21G18A-AUT | QFN-48-1EP_7x7mm_P0.5mm_EP5.15x5.15mm | 1 | http://ww1.microchip.com/downloads/en/DeviceDoc/SAMD21-Family-DataSheet-DS40001882D.pdf | ATSAMD21G18A-MUT | ATSAMD21G18A-MUTCT-ND | https://www.digikey.com/product-detail/en/microchip-technology/ATSAMD21G18A-MUT/ATSAMD21G18A-MUTCT-ND/4878880
24 | InvenSense 9-Axis Motion Sensor, Accelerometer, Gyroscope, Compass, I2C/SPI, QFN-24 | ICM-20948 | U3 | ICM-20948 | InvenSense_QFN-24_3x3mm_P0.4mm | 1 | http://www.invensense.com/wp-content/uploads/2016/06/DS-000189-ICM-20948-v1.3.pdf | ICM-20948 | 1428-1123-1-ND
25 |  | MAX1726EUK18+ | U5 | MAX1726EUK18+ | SOT-23-5 | 1 |  | MAX1726EUK18+T | MAX1726EUK18+T-ND
26 |  | MAX828 | U2 | MAX828 | SOT-23-5 | 1 |  | MAX828EUK+T | MAX828EUK+TCT-ND
27 | FRAM memory with SPI interface, SOIC-8 SON-8 | MB85RSxM_WLP8 | U9 | MB85RSxM_WLP8 | BGA8CP30X40_5X3_309X228X35B25N | 1 | http://www.fujitsu.com/downloads/MICRO/fsa/pdf/products/memory/fram/MB85RS16-DS501-00014-6v0-E.pdf | MB85RS1MTPW-G-APEWE1 | 865-1272-2-ND
28 | Single cell, Li-Ion/Li-Po charge management controller, 4.20V, Tri-State Status Output, in SOT23-5 package | MCP73831-2-OT | U1 | MCP73831-2-OT | SOT-23-5 | 1 | http://ww1.microchip.com/downloads/en/DeviceDoc/20001984g.pdf | MCP73831T-2ATI/OT | MCP73831T-2ATI/OTCT-ND
29 |  | SN74AUP1G98 | U8 | SN74AUP1G98 | SOT-23-6 | 1 |  | SN74AUP1G98DBVR | 296-19087-1-ND
30 | 500mA Low drop-out regulator, Fixed Output 3.3V, SOT-23-5 | SPX3819M5-L-3-3 | U4 | SPX3819M5-L-3-3 | SOT-23-5 | 1 | https://www.exar.com/content/document.ashx?id=22106&languageid=1033&type=Datasheet&partnumber=SPX3819&filename=SPX3819.pdf&part=SPX3819 | SPX3819M5-L-3-3/TR | 1016-1873-1-ND
31 |  | SiT1532 | U10 | SiT1532 | SiT1532 | 1 |  | SIT1532AI-J4-DCC-32.768E | 1473-1240-1-ND
32 | Two pin crystal | Crystal | Y1 | Crystal | Crystal_SMD_3215-2Pin_3.2x1.5mm | 1 | ~ | FC-135 32.7680KA-A5 | SER4103CT-ND
Component Groups: | 32
Component Count: | 76
Fitted Components: | 76
Number of PCBs: | 1
Total components: | 76
Schematic Version:
Schematic Date:
BoM Date: | Wednesday, January 08, 2020 at 03:53:28 PM
Schematic Source: | /Users/matt/Box Sync/Biologging/Technology/ARBO Mini/ARBO Mini.sch
KiCad Version: | Eeschema (5.1.2-1)-1

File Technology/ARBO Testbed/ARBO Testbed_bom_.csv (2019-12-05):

Component | Description | Part | References | Value | Footprint | Quantity Per PCB | Datasheet | Manufacturer Part Number | Digi-key Part Number | Link
1 | Unpolarized capacitor | C | C11 C15 C18 C19 C22 C32 C35 | 0.1uF | C_0402_1005Metric | 7 | ~ | LMK105BJ104KV-F | 587-1227-1-ND
2 | Unpolarized capacitor | C | C13 C14 C20 C21 C25 C26 C27 C29 C30 C38 | 1000pF | C_0402_1005Metric | 10 | ~ | GRM1555C1H102JA01J | 490-6190-1-ND
3 | Unpolarized capacitor | C | C5 C6 C7 C23 | 10uF | C_0603_1608Metric | 4 | ~ | GRM155R60E106ME16D | 490-10692-1-ND
4 | Unpolarized capacitor | C | C1 C2 C3 C8 C16 C31 C34 C36 C37 | 1uF | C_0402_1005Metric | 9 | ~ | C0402C105K9PACTU | 399-4873-1-ND
5 | Unpolarized capacitor | C | C33 | 22uF | C_0603_1608Metric | 1 | ~ | GRM188R60J226MEA0D | 490-7611-1-ND
6 | Polarized capacitor, US symbol | CP1 | C4 C9 C10 | 3.3uF | C_0402_1005Metric | 3 | ~ | C1005X5R0G335K050BB | 445-5948-1-ND
7 | Unpolarized capacitor | C | C12 C17 C24 C28 | 4.7nF | C_0402_1005Metric | 4 | ~ | C0402C472K4RECAUTO | 399-17875-1-ND
8 |  | JST-PH | CONN1 | JST-PH | JST_SHL_SM02B-SHLS-TF_1x02-1MP_P1.00mm_Horizontal | 1 |  | SM02B-SHLS-TF(LF)(SN) | 455-3957-1-ND
9 | Light emitting diode | LED | D2 | GRN | LED_0603_1608Metric | 1 | ~ | LTST-C191KGKT | 160-1446-1-ND
10 | Schottky diode | D_Schottky | D1 | MBR120 | D_SOD-123F | 1 | https://www.digikey.com/product-detail/en/on-semiconductor/MBR120VLSFT1G/MBR120VLSFT1GOSCT-ND/893874 | MBR120VLSFT1G | MBR120VLSFT1GOSCT-ND
11 | Light emitting diode | LED | D4 | ORG | LED_0603_1608Metric | 1 | ~ | LTST-C191KFKT | 160-1445-1-ND
12 | Light emitting diode | LED | D3 | RED | LED_0603_1608Metric | 1 | ~ | LTST-C191KRKT | 160-1447-1-ND
13 | Generic screw terminal, single row, 01x02, script generated (kicad-library-utils/schlib/autogen/connector/) | Screw_Terminal_01x02 | J3 J4 J5 J6 J7 | IN1 | TerminalBlock_Phoenix_PT-1,5-2-3.5-H_1x02_P3.50mm_Horizontal | 5 | ~ | 1776275-2 | A98036-ND
14 | Micro SD Card Socket with card detection pins | Micro_SD_Card_473093351 | J2 | Micro_SD_Card_473093351 | 473093351_uSDCard | 1 | https://www.hirose.com/product/en/download_file/key_name/DM3/category/Catalog/doc_file_id/49662/?file_category_id=4&item_id=195&is_series=1 | 0473093351 | WM10795CT-ND
15 | USB Micro Type B connector | USB_B_Micro | J1 | USB_B_Micro | USB_Micro-B_Molex-105017-0001 | 1 | ~ | 1050170001 | WM1399CT-ND
16 | Resistor | R | R1 R5 | 100K | R_0603_1608Metric | 2 | ~ | RR0816P-104-D | RR08P100KDCT-ND
17 | Resistor | R | R3 R4 R8 R9 | 10K | R_0603_1608Metric | 4 | ~ | RC0603JR-0710KL | 311-10KGRCT-ND
18 | Resistor | R | R2 R6 | 1K | R_0603_1608Metric | 2 | ~ | RC0603JR-071KL | 311-1.0KGRCT-ND
19 | Resistor | R | R16 | 1M | R_0603_1608Metric | 1 | ~ | RC0603FR-071ML | 311-1.00MHRCT-ND
20 | Resistor | R | R7 R10 R11 R12 R13 R14 R15 R17 R18 | 2.2K | R_0603_1608Metric | 9 | ~ | ERJ-3GEYJ222V | P2.2KGCT-ND
21 | Single Pole Single Throw (SPST) switch | SW_SPST | SW1 | SW_SPST | SW_SPST_PTS810 | 1 | ~ | PTS810 SJK 250 SMTR LFS | CKN10503TR-ND
22 |  | ADS1294_TQFP | U7 | ADS1294 | TQFP-64-1EP_10x10mm_P0.5mm_EP8x8mm | 1 |  | ADS1294IPAG | 296-27932-ND
23 | SAM D21 Microchip SMART ARM-based Flash MCU, 48Mhz, 256K Flash, 32K SRAM, TQFP-48 | ATSAMD21G18A-AUT | U6 | ATSAMD21G18A-AUT | QFN-48-1EP_7x7mm_P0.5mm_EP5.15x5.15mm | 1 | http://ww1.microchip.com/downloads/en/DeviceDoc/SAMD21-Family-DataSheet-DS40001882D.pdf | ATSAMD21G18A-MUT | ATSAMD21G18A-MUTCT-ND | https://www.digikey.com/product-detail/en/microchip-technology/ATSAMD21G18A-MUT/ATSAMD21G18A-MUTCT-ND/4878880
24 |  | MAX1726EUK18+ | U5 | MAX1726EUK18+ | SOT-23-5 | 1 |  | MAX1726EUK18+T | MAX1726EUK18+T-ND
25 |  | MAX828 | U2 | MAX828 | SOT-23-5 | 1 |  | MAX828EUK+T | MAX828EUK+TCT-ND
26 | FRAM memory with SPI interface, SOIC-8 SON-8 | MB85RS16 | U9 | MB85RS1M | SOIC-8_3.9x4.9mm_P1.27mm | 1 | http://www.fujitsu.com/downloads/MICRO/fsa/pdf/products/memory/fram/MB85RS16-DS501-00014-6v0-E.pdf | MB85RS1MTPNF-G-JNERE1 | 865-1255-1-ND
27 | Single cell, Li-Ion/Li-Po charge management controller, 4.20V, Tri-State Status Output, in SOT23-5 package | MCP73831-2-OT | U1 | MCP73831-2-OT | SOT-23-5 | 1 | http://ww1.microchip.com/downloads/en/DeviceDoc/20001984g.pdf | MCP73831T-2ATI/OT | MCP73831T-2ATI/OTCT-ND
28 | InvenSense 9-Axis Motion Sensor, Accelerometer, Gyroscope, Compass, I2C/SPI | MPU-9250 | U3 | MPU-9250 | InvenSense_QFN-24_3x3mm_P0.4mm | 1 | https://store.invensense.com/datasheets/invensense/MPU9250REV1.0.pdf | MPU-9250 | 1428-1019-1-ND
29 |  | SN74AUP1G98 | U8 | SN74AUP1G98 | SOT-23-6 | 1 |  | SN74AUP1G98DBVR | 296-19087-1-ND
30 | 500mA Low drop-out regulator, Fixed Output 3.3V, SOT-23-5 | SPX3819M5-L-3-3 | U4 | SPX3819M5-L-3-3 | SOT-23-5 | 1 | https://www.exar.com/content/document.ashx?id=22106&languageid=1033&type=Datasheet&partnumber=SPX3819&filename=SPX3819.pdf&part=SPX3819 | SPX3819M5-L-3-3/TR | 1016-1873-1-ND
31 | Two pin crystal | Crystal | Y1 | Crystal | Crystal_SMD_3215-2Pin_3.2x1.5mm | 1 | ~ | FC-135 32.7680KA-A5 | SER4103CT-ND
Component Groups: | 31
Component Count: | 79
Fitted Components: | 79
Number of PCBs: | 1
Total components: | 79
Schematic Version:
Schematic Date:
BoM Date: | Wednesday, December 04, 2019 at 03:34:32 PM
Schematic Source: | /Users/matt/Box Sync/Biologging/Technology/ARBO Testbed/ARBO Testbed.sch
KiCad Version: | Eeschema (5.1.2-1)-1

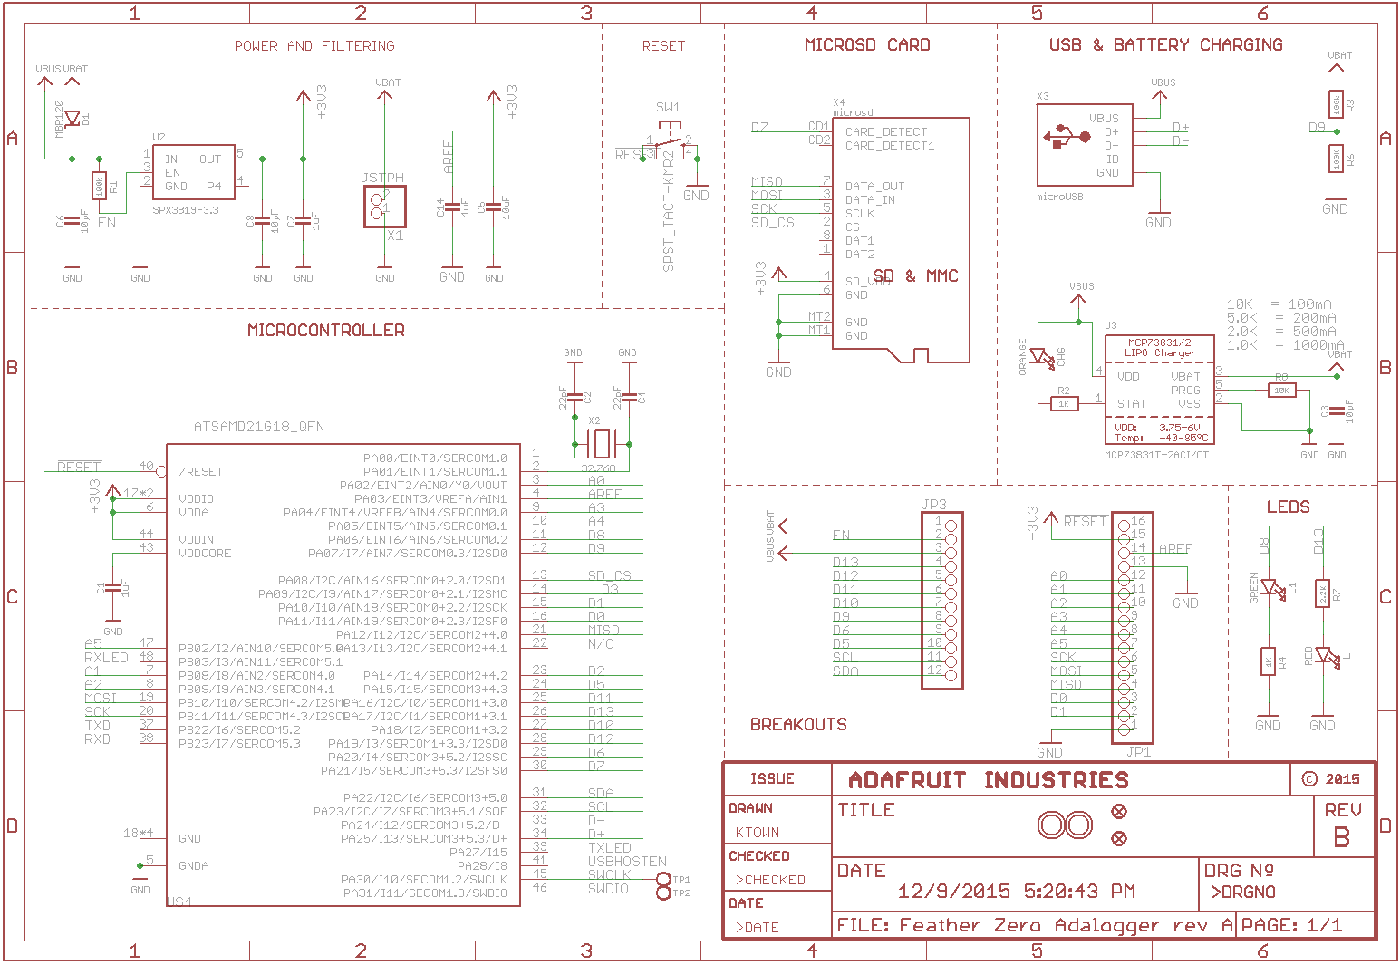
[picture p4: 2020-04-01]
Technology/NUTS/NUTS_PCB/Components/SAMD21G_adafruit_products_schem.png

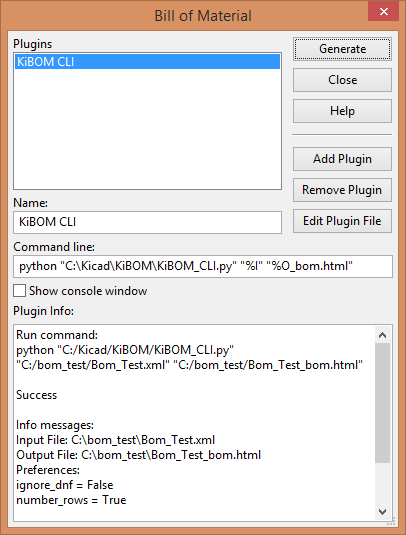
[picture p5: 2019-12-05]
Technology/KiCad/KiBoM/example/bom.png

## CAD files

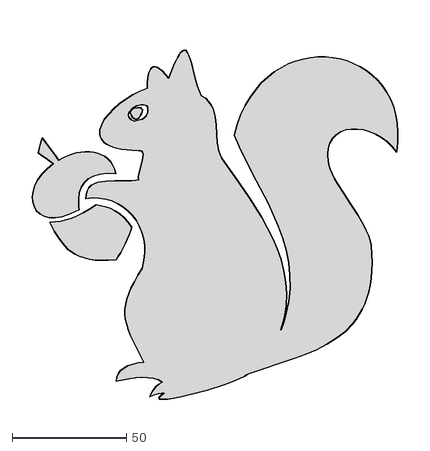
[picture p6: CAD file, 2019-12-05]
Technology/ARBO Testbed/squirrel-with-acorn.dxf
174.4 x 173.1

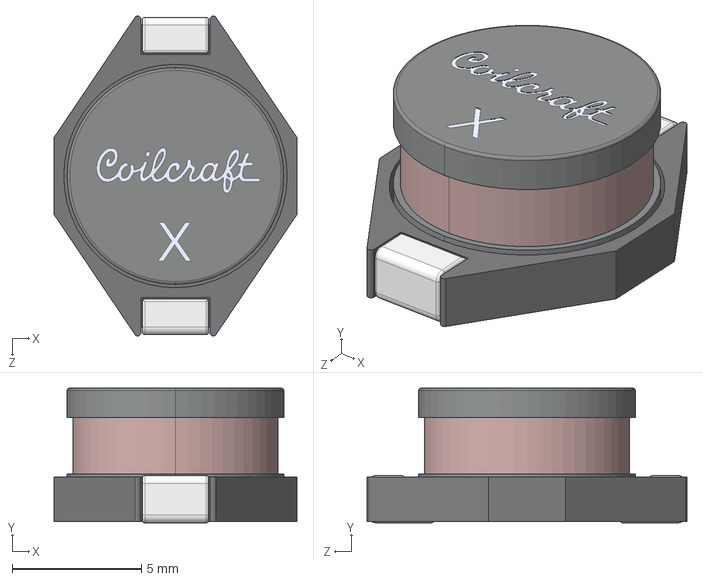
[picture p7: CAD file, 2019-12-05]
Technology/KiCad/ARBO Parts/Coilcraft-PA6512-AE.step
9.40 x 5.21 x 12.4 mm

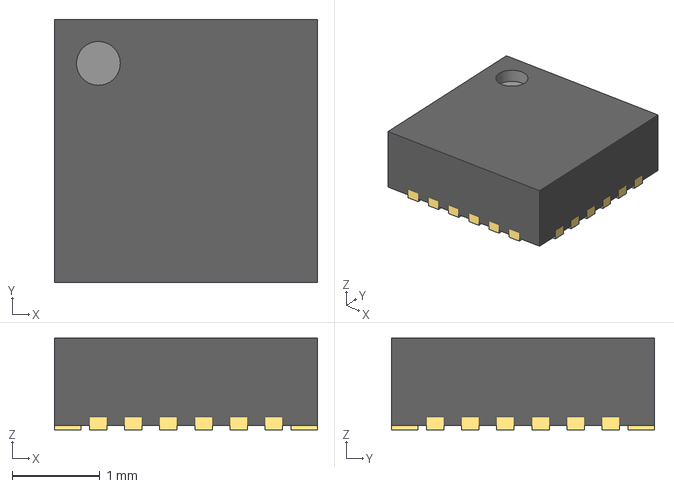
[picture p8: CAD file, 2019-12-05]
Technology/KiCad/ARBO Parts/qfn-24-3x3mm-1.snapshot.1/QFN-24 3x3 0.4mm.stp
3.00 x 3.00 x 1.05 mm

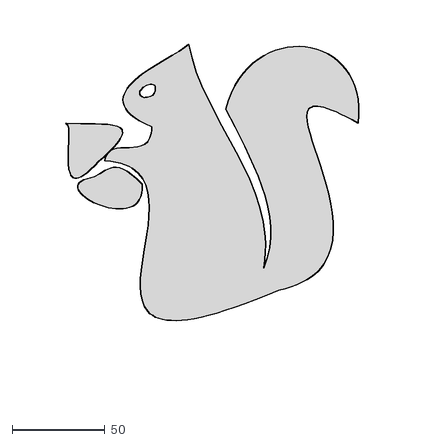
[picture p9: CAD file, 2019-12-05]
Technology/ARBO Testbed/squirrel-with-acorn_simple.dxf
219.2 x 207.8

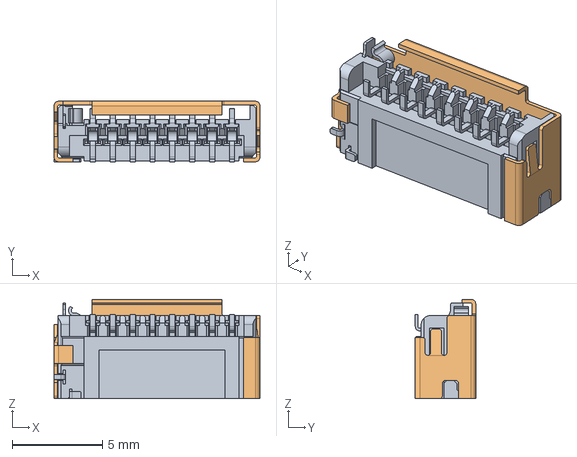
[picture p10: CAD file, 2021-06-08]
Technology/Components/uSD Card/473093351.stp
11.4 x 3.35 x 5.50 mm

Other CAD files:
Technology/KiCad/ARBO Parts/qfn-24-3x3mm-1.snapshot.1/QFN-24 3x3 0.4mm.ipt

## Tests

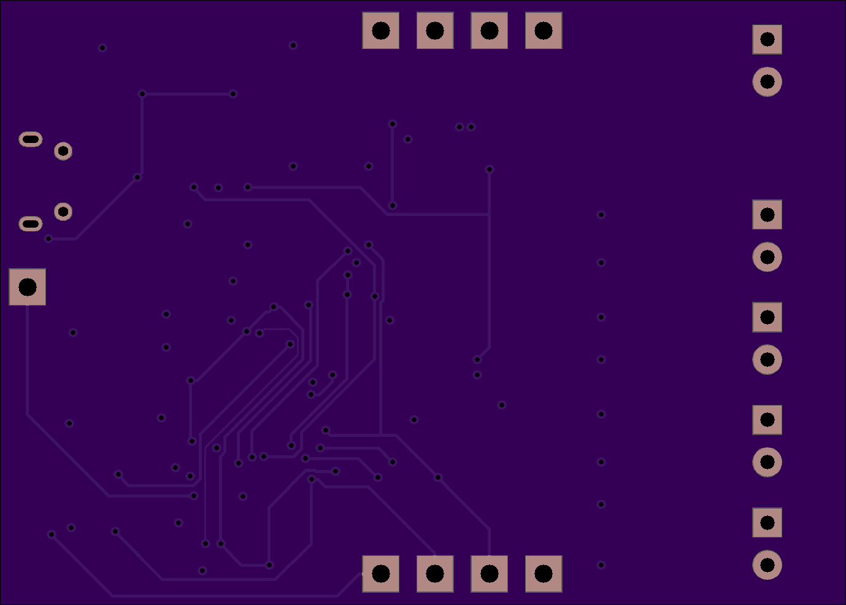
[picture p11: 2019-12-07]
assets/images/ARBO_testbed_back.png

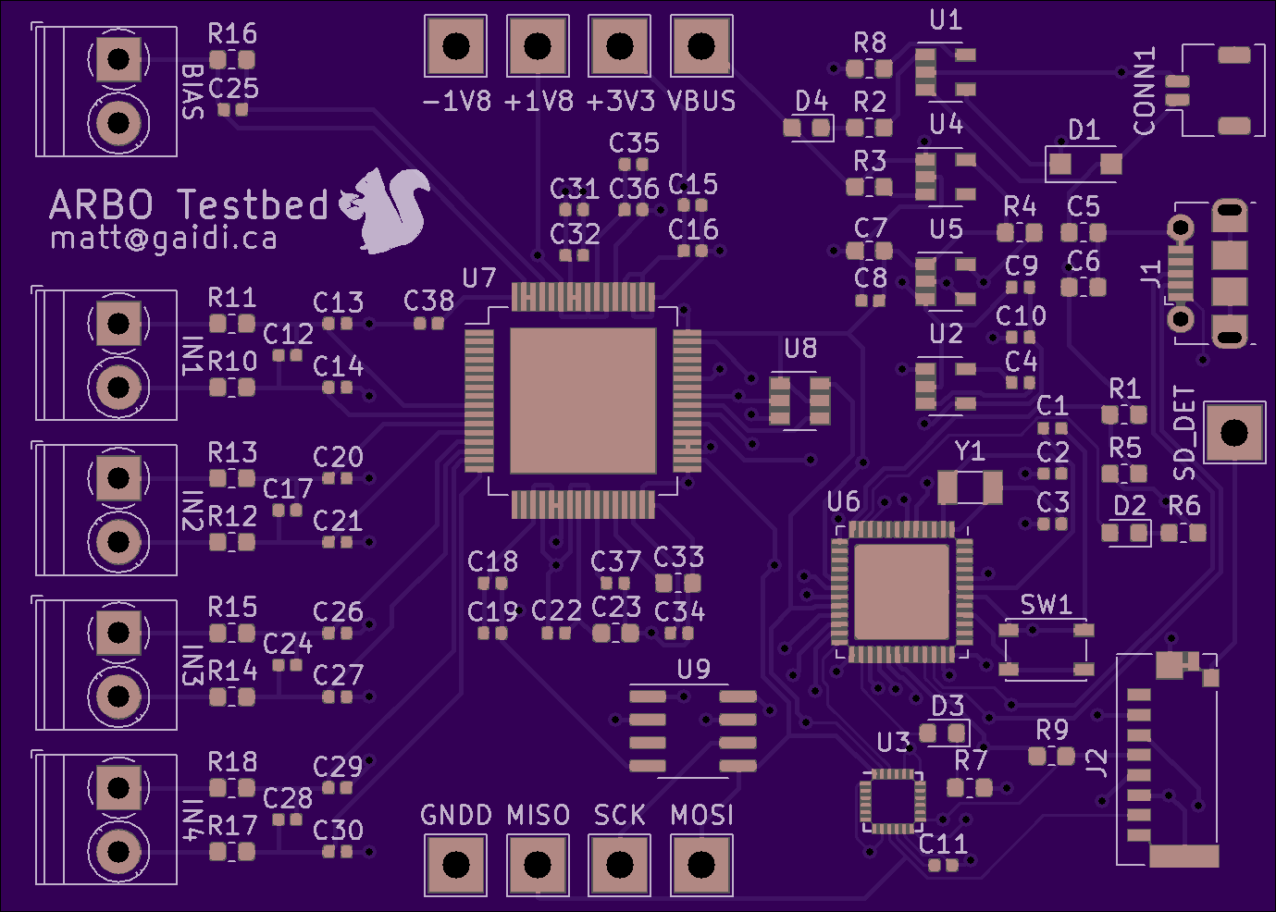
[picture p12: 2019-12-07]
assets/images/ARBO_testbed_front.png

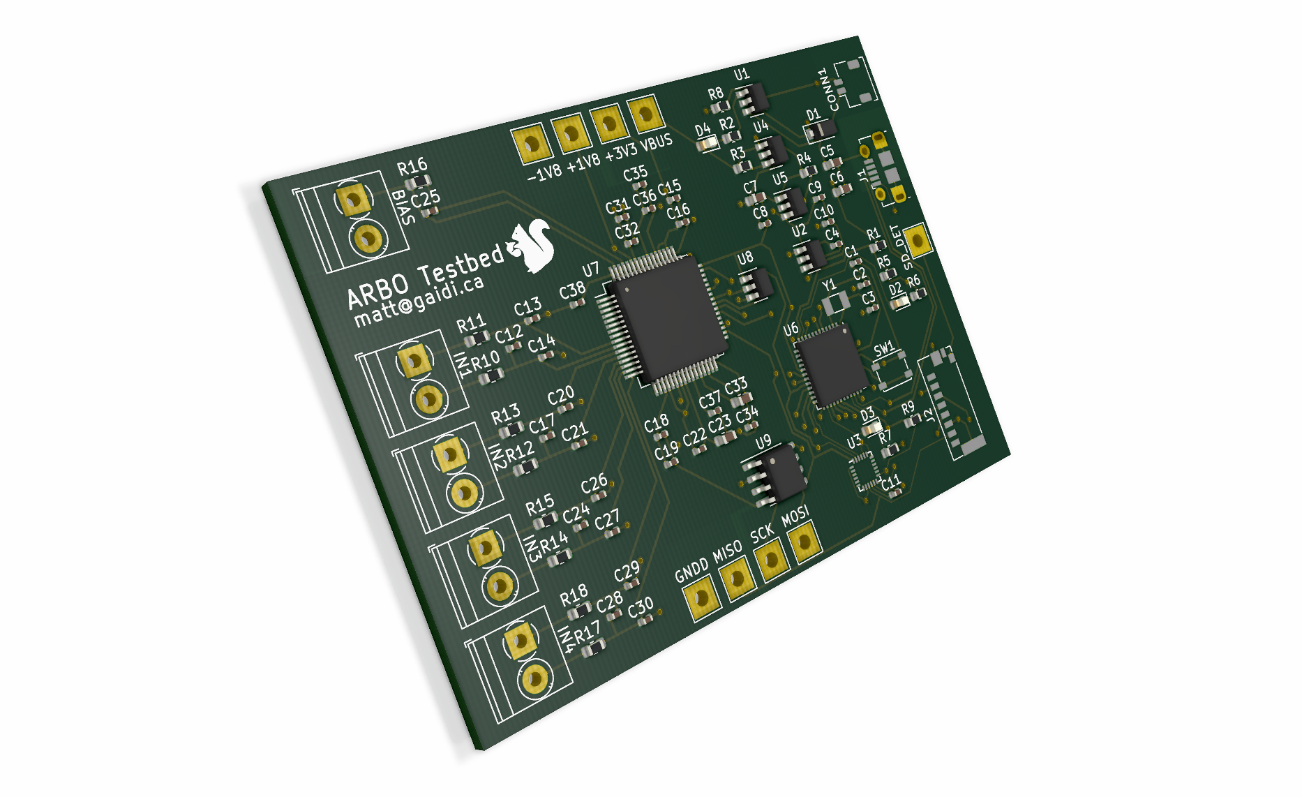
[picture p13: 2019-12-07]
assets/images/ARBO_testbed_pcb_render.png

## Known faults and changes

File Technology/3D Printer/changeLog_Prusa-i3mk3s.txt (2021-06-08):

20200316
- 3D printer delivered by Chris
- Auto-home was not working, wouldn't calibrate, grinding sound on y-axis
- Tried loosening y-axis belt a little, no change
- Tried loosening y-axis u-bolt (bearing), no change
- Found y-axis was binding without motor/belt attached
-- Removed heatbed, removed y-axis plate: bearings still binding to rods
-- Removed and cleaned rods with isopropyl, no change
-- Oiled bearings and rods, now they glide freely! Put back together
- Everything works: re-calibrated xyz, first layer (didn't realize filament was PETG)
-- only calibrating/testing with supplied filament
- Successfully printed PETG squirrel, switching to own PLA filament

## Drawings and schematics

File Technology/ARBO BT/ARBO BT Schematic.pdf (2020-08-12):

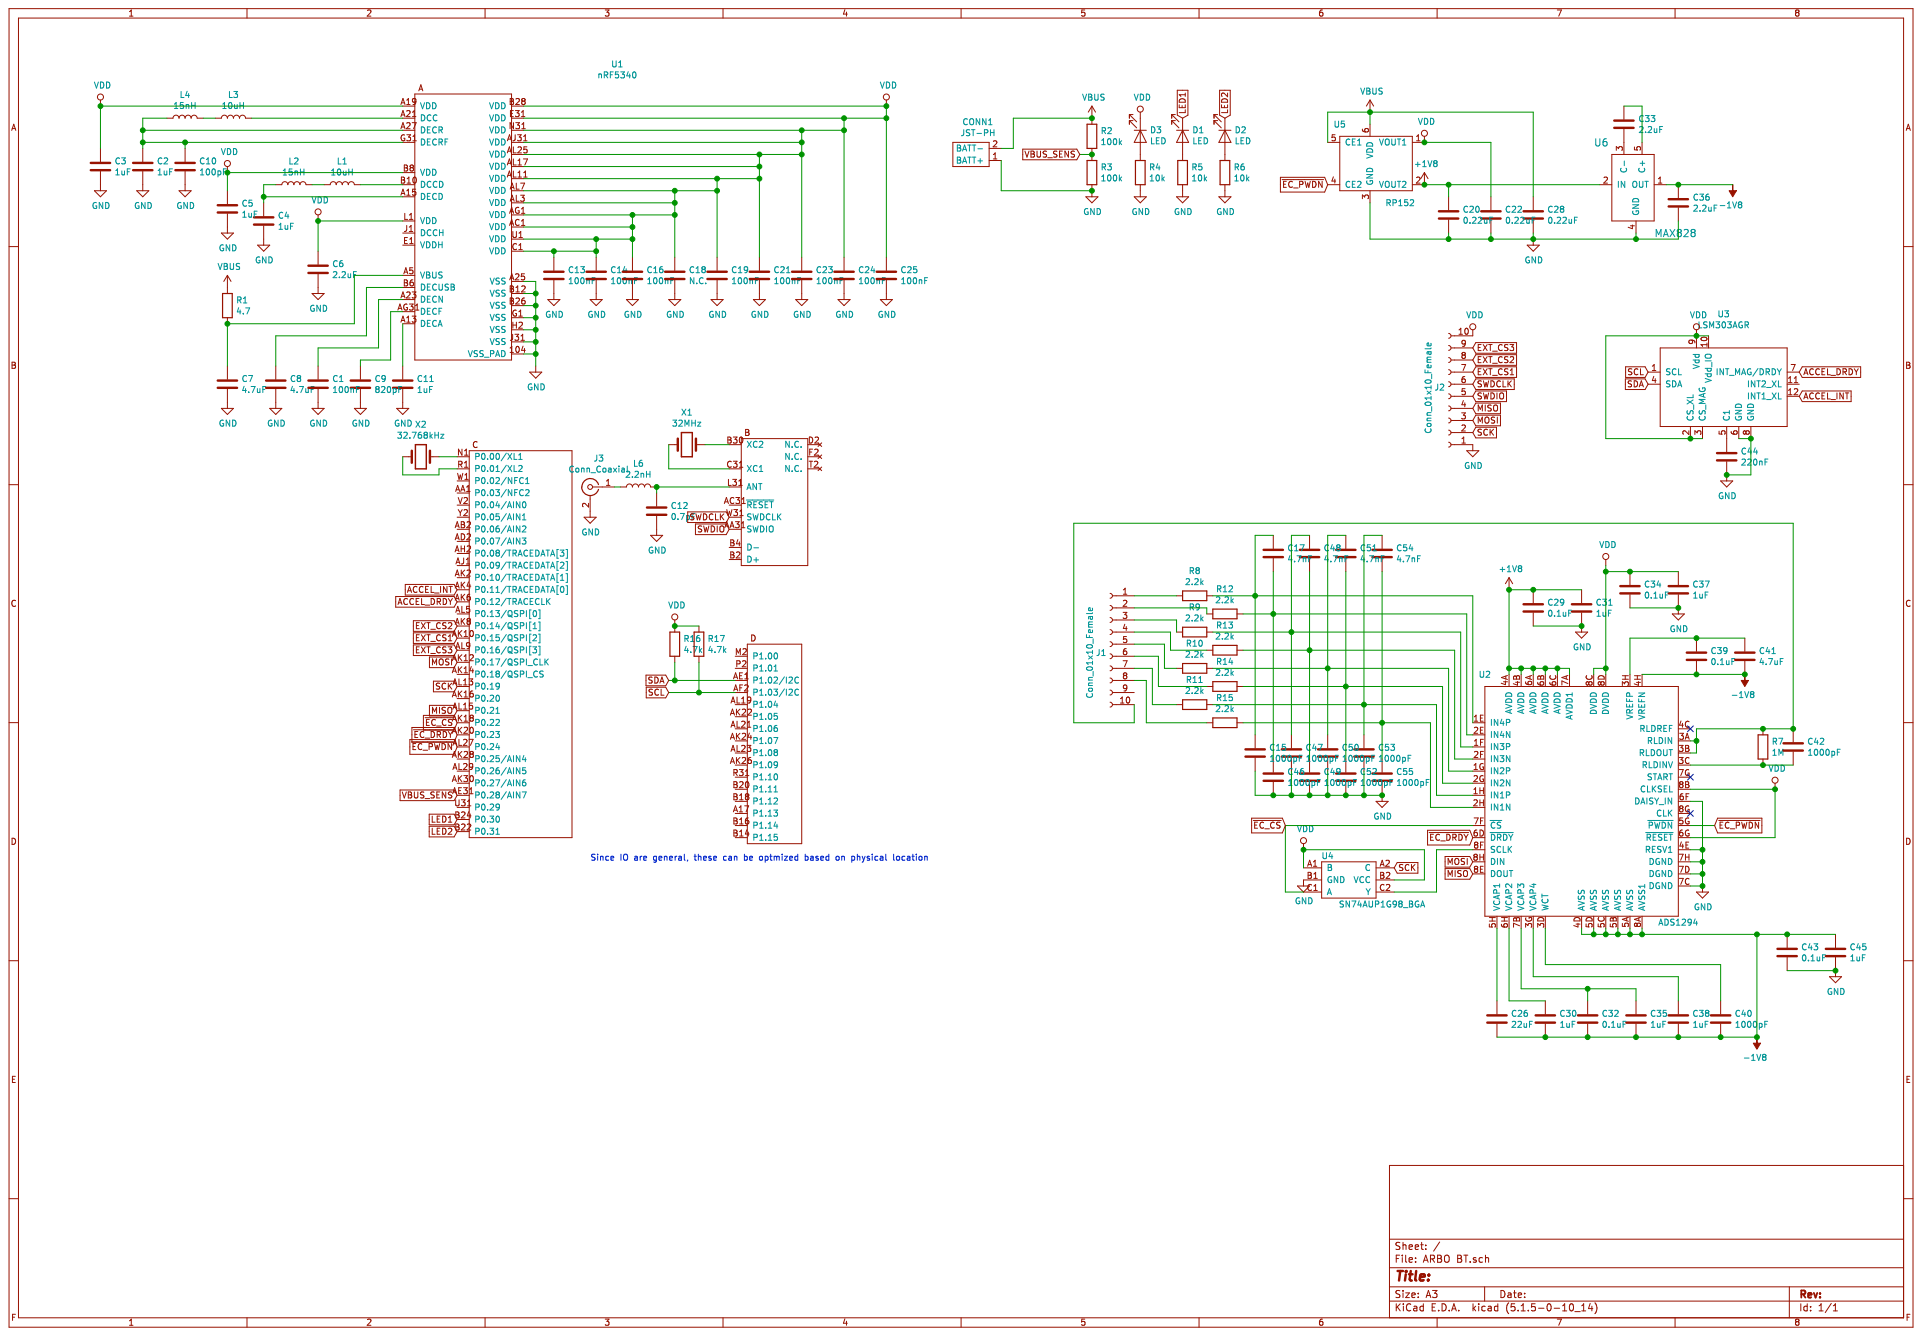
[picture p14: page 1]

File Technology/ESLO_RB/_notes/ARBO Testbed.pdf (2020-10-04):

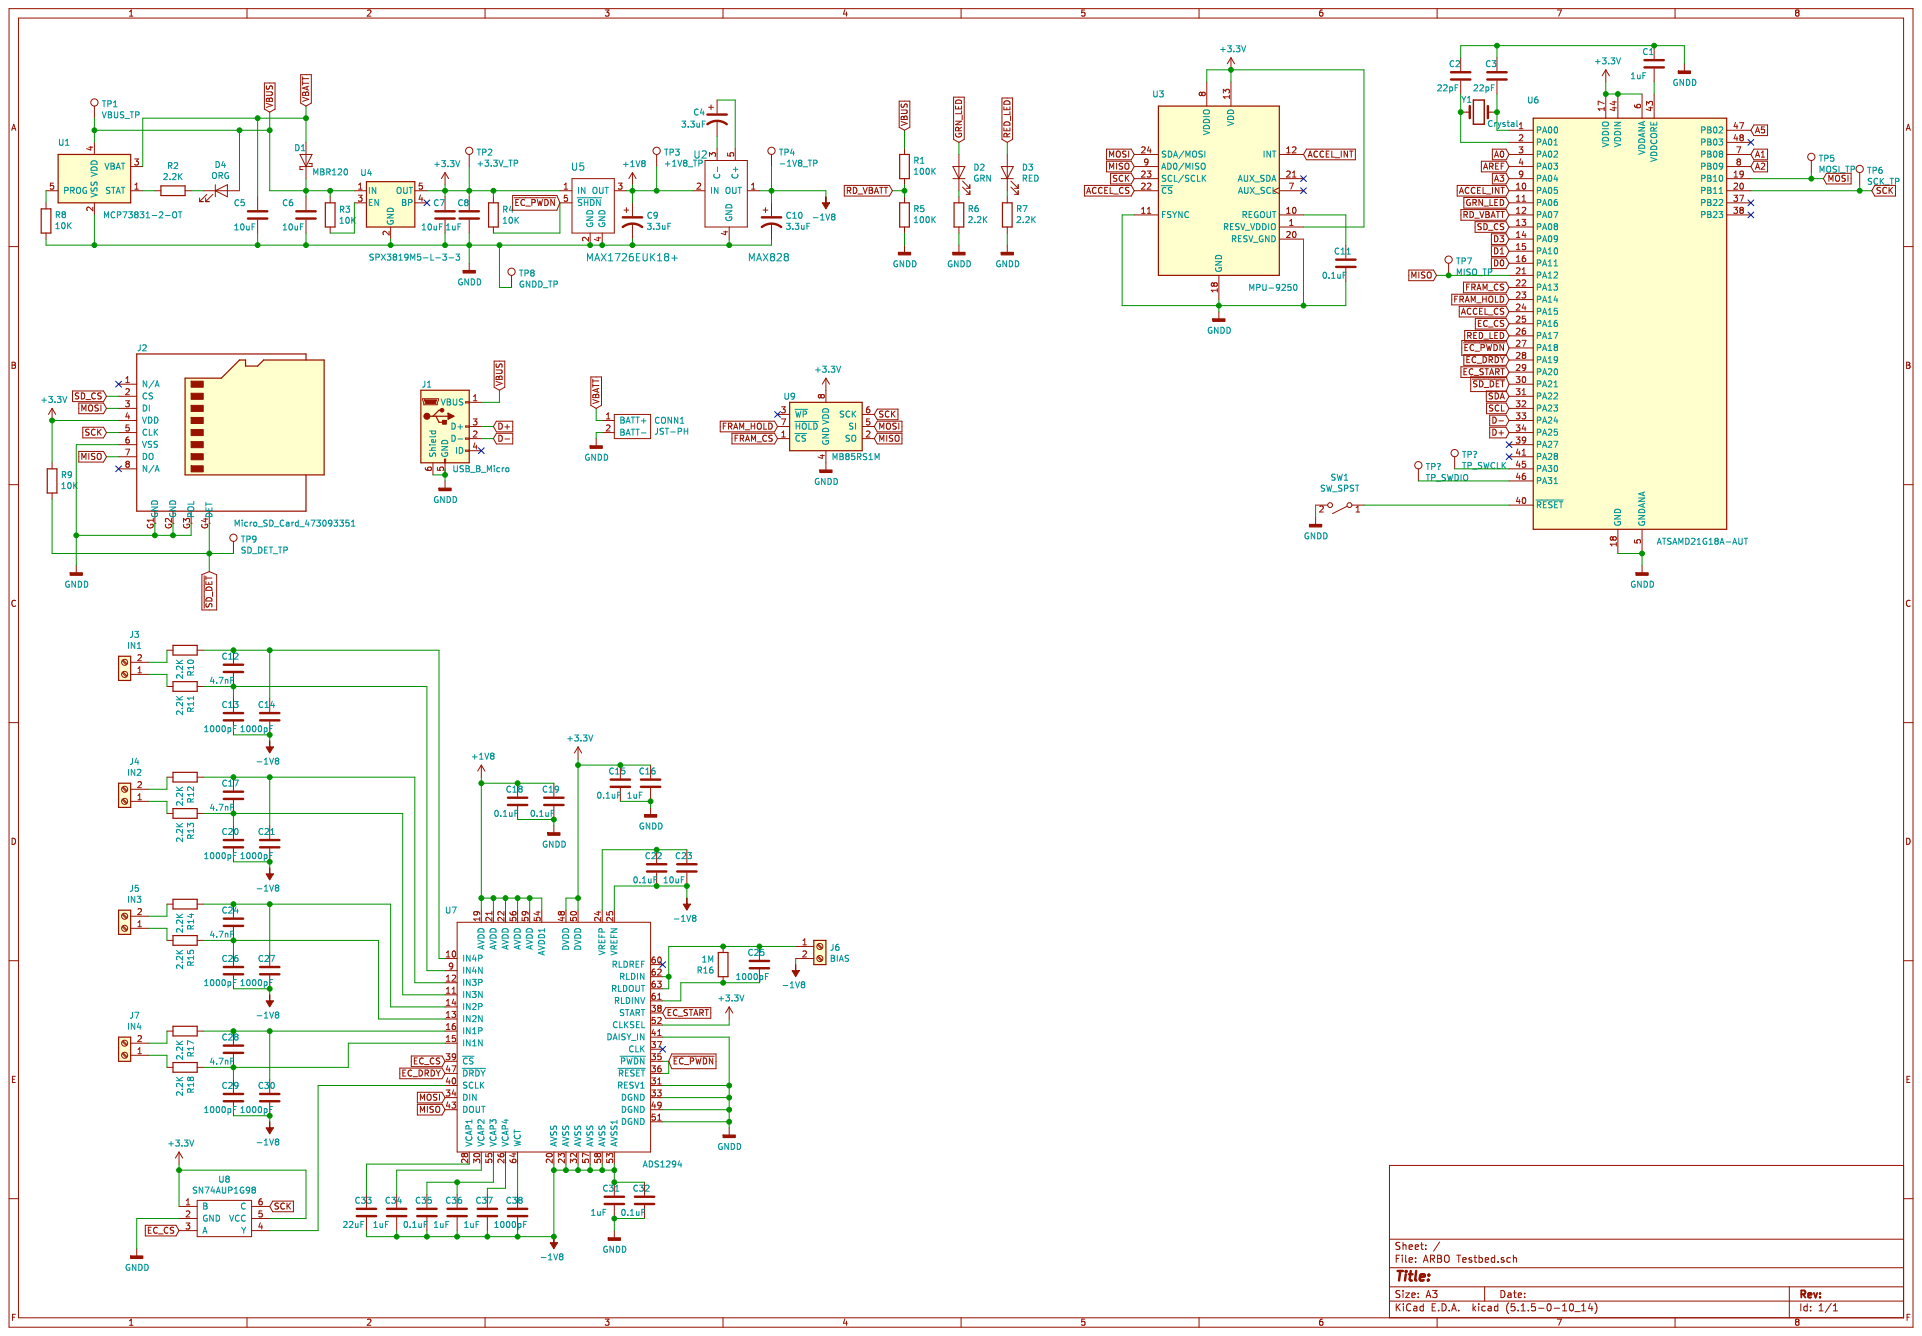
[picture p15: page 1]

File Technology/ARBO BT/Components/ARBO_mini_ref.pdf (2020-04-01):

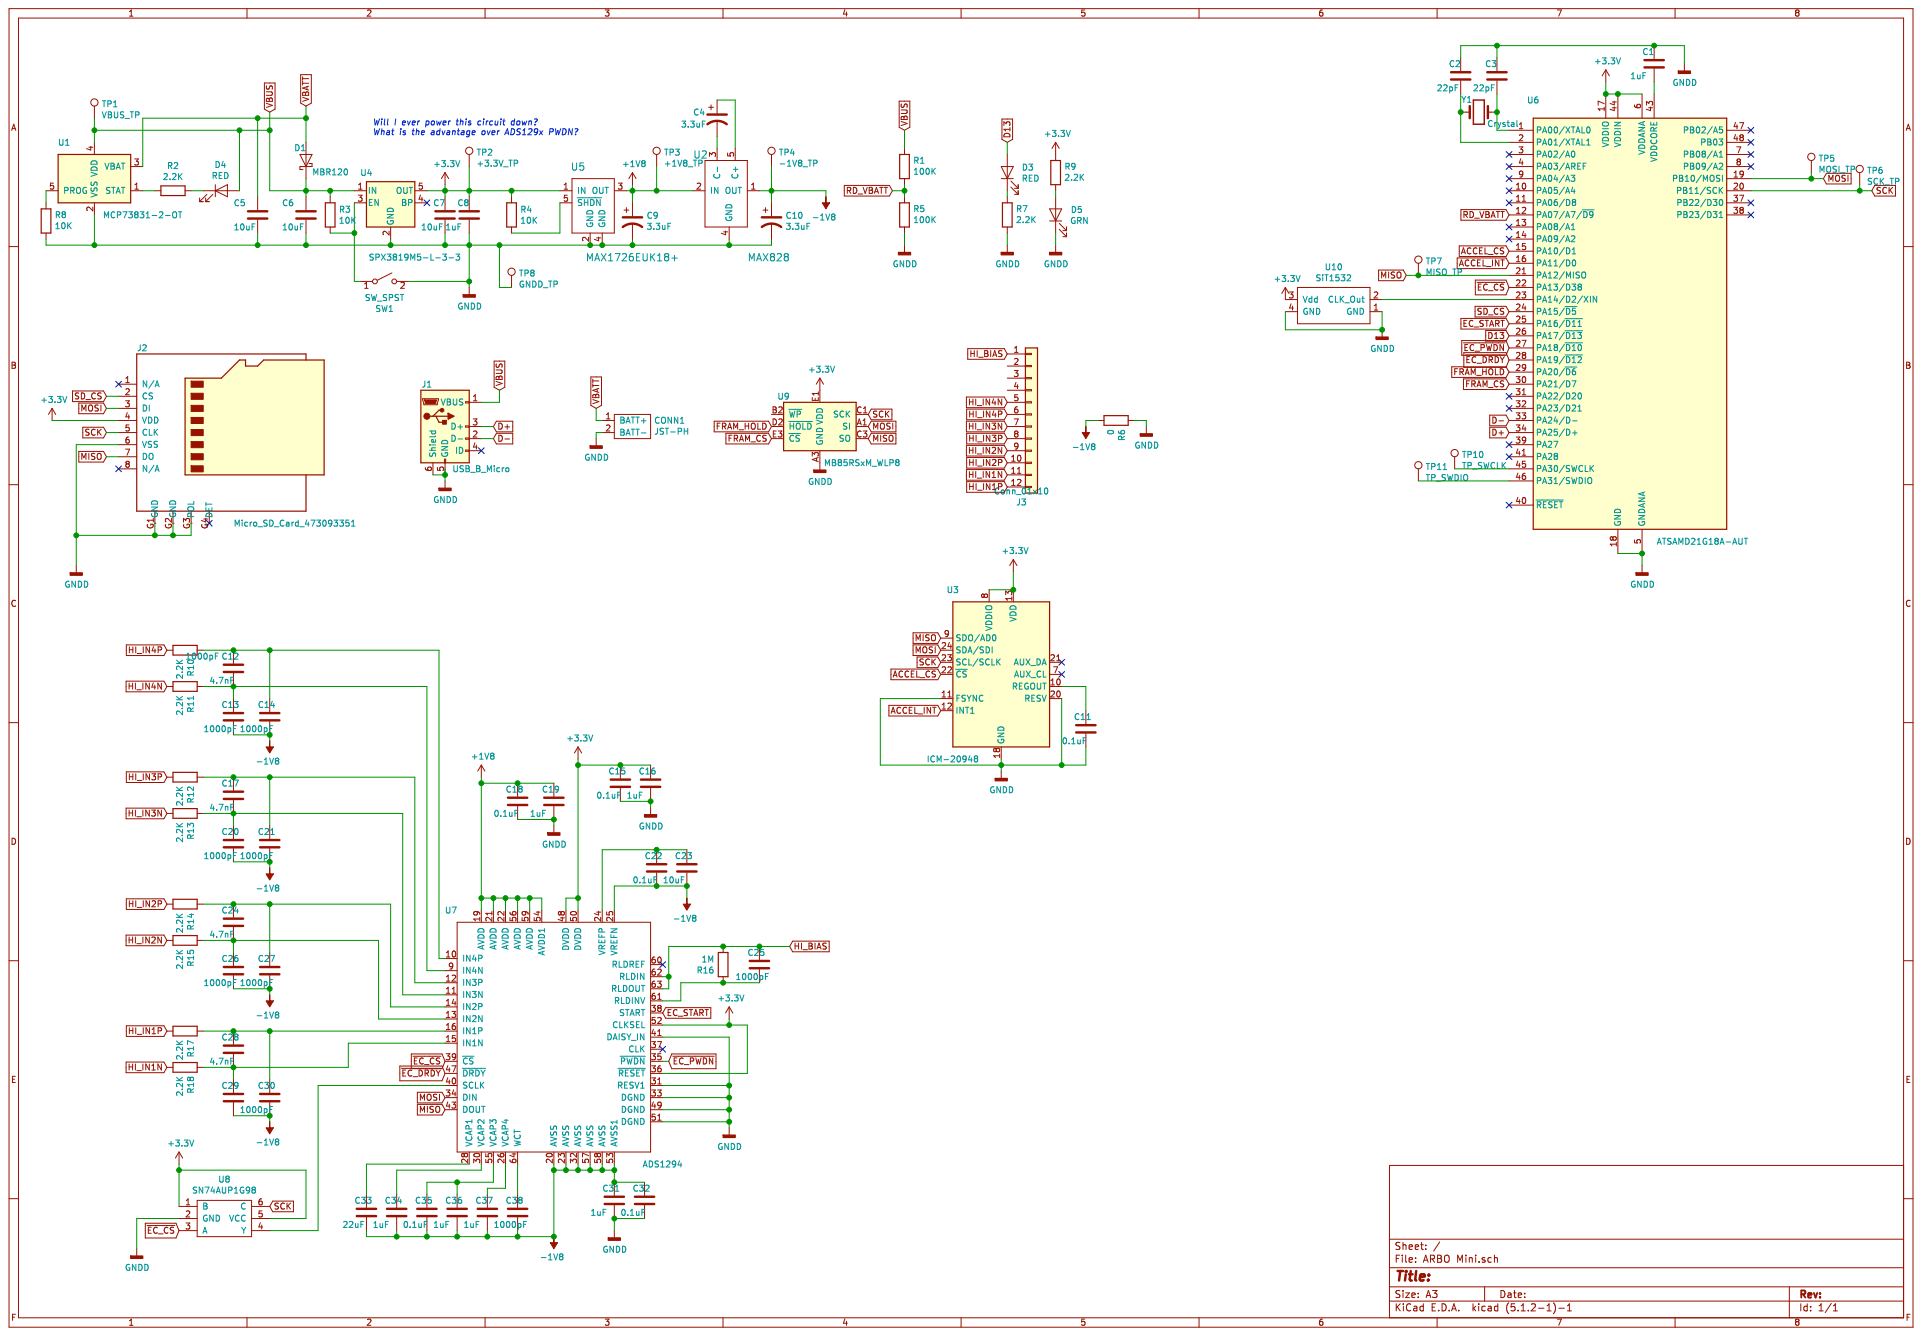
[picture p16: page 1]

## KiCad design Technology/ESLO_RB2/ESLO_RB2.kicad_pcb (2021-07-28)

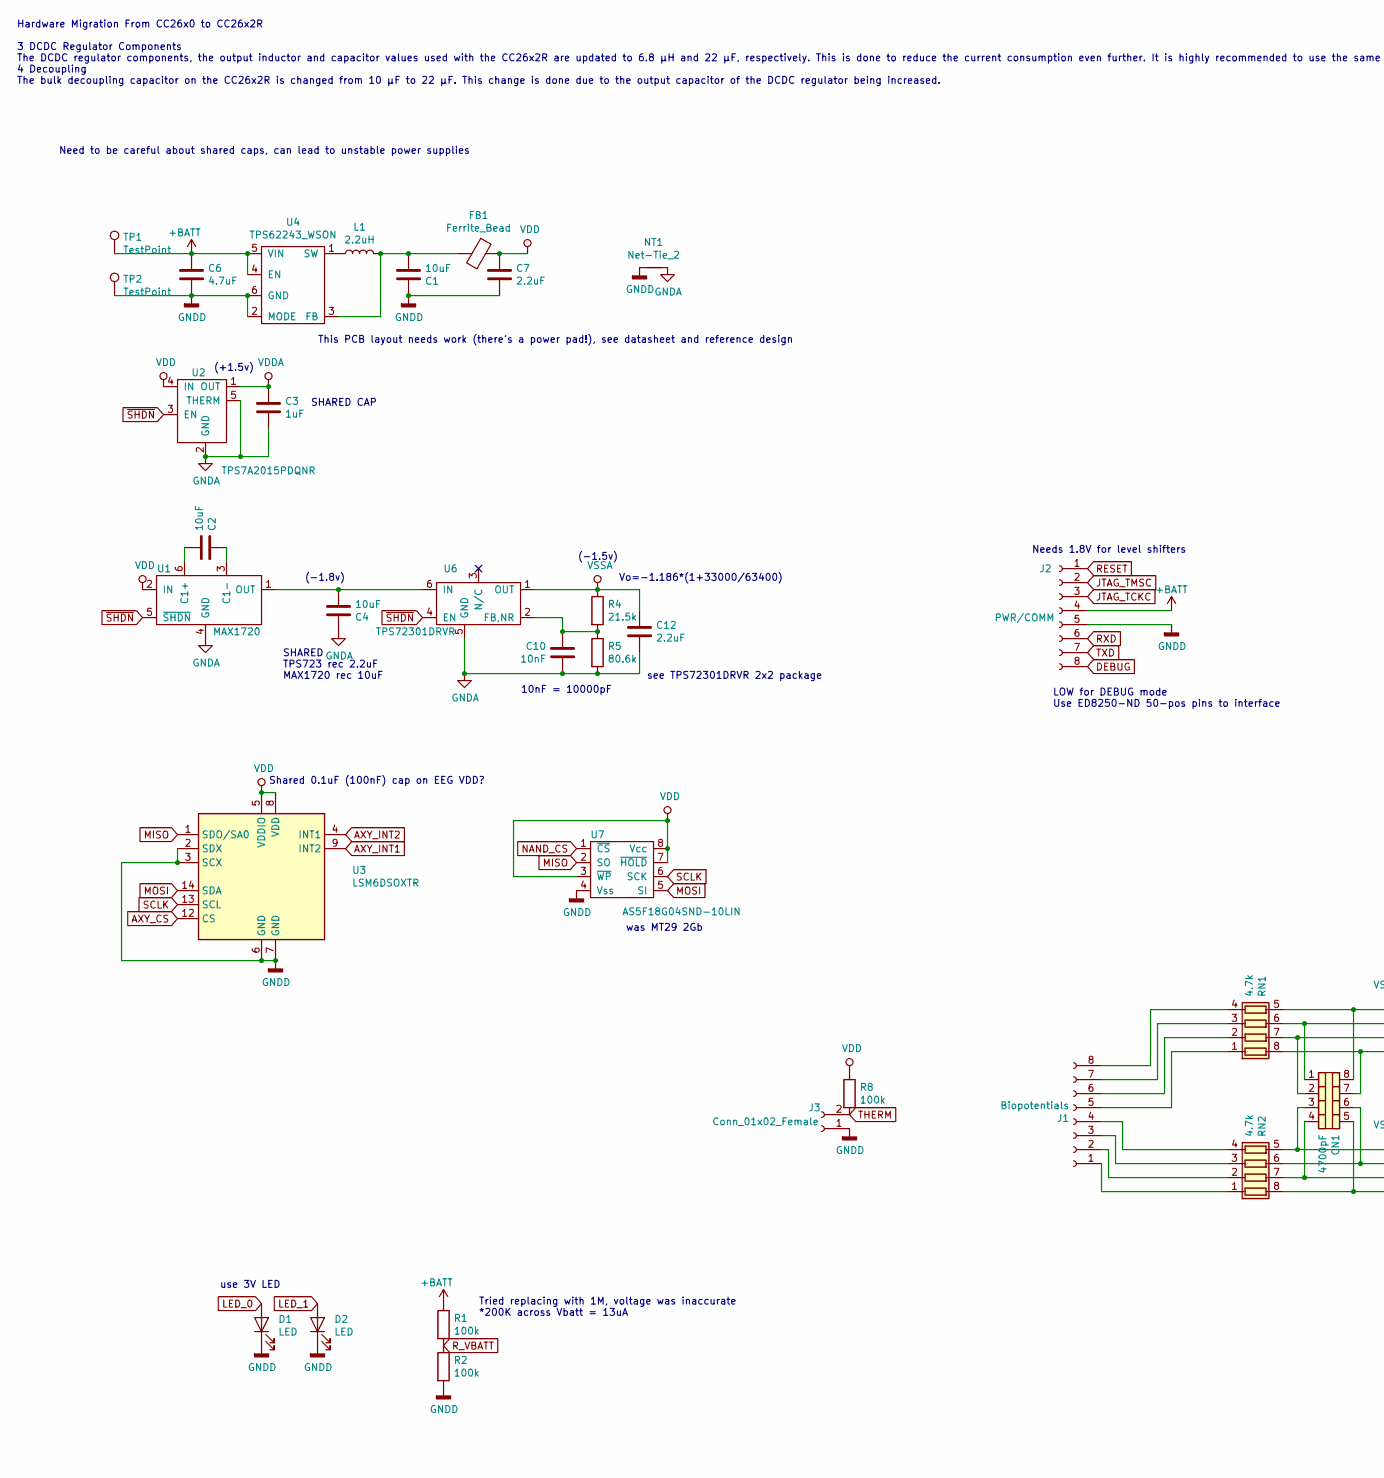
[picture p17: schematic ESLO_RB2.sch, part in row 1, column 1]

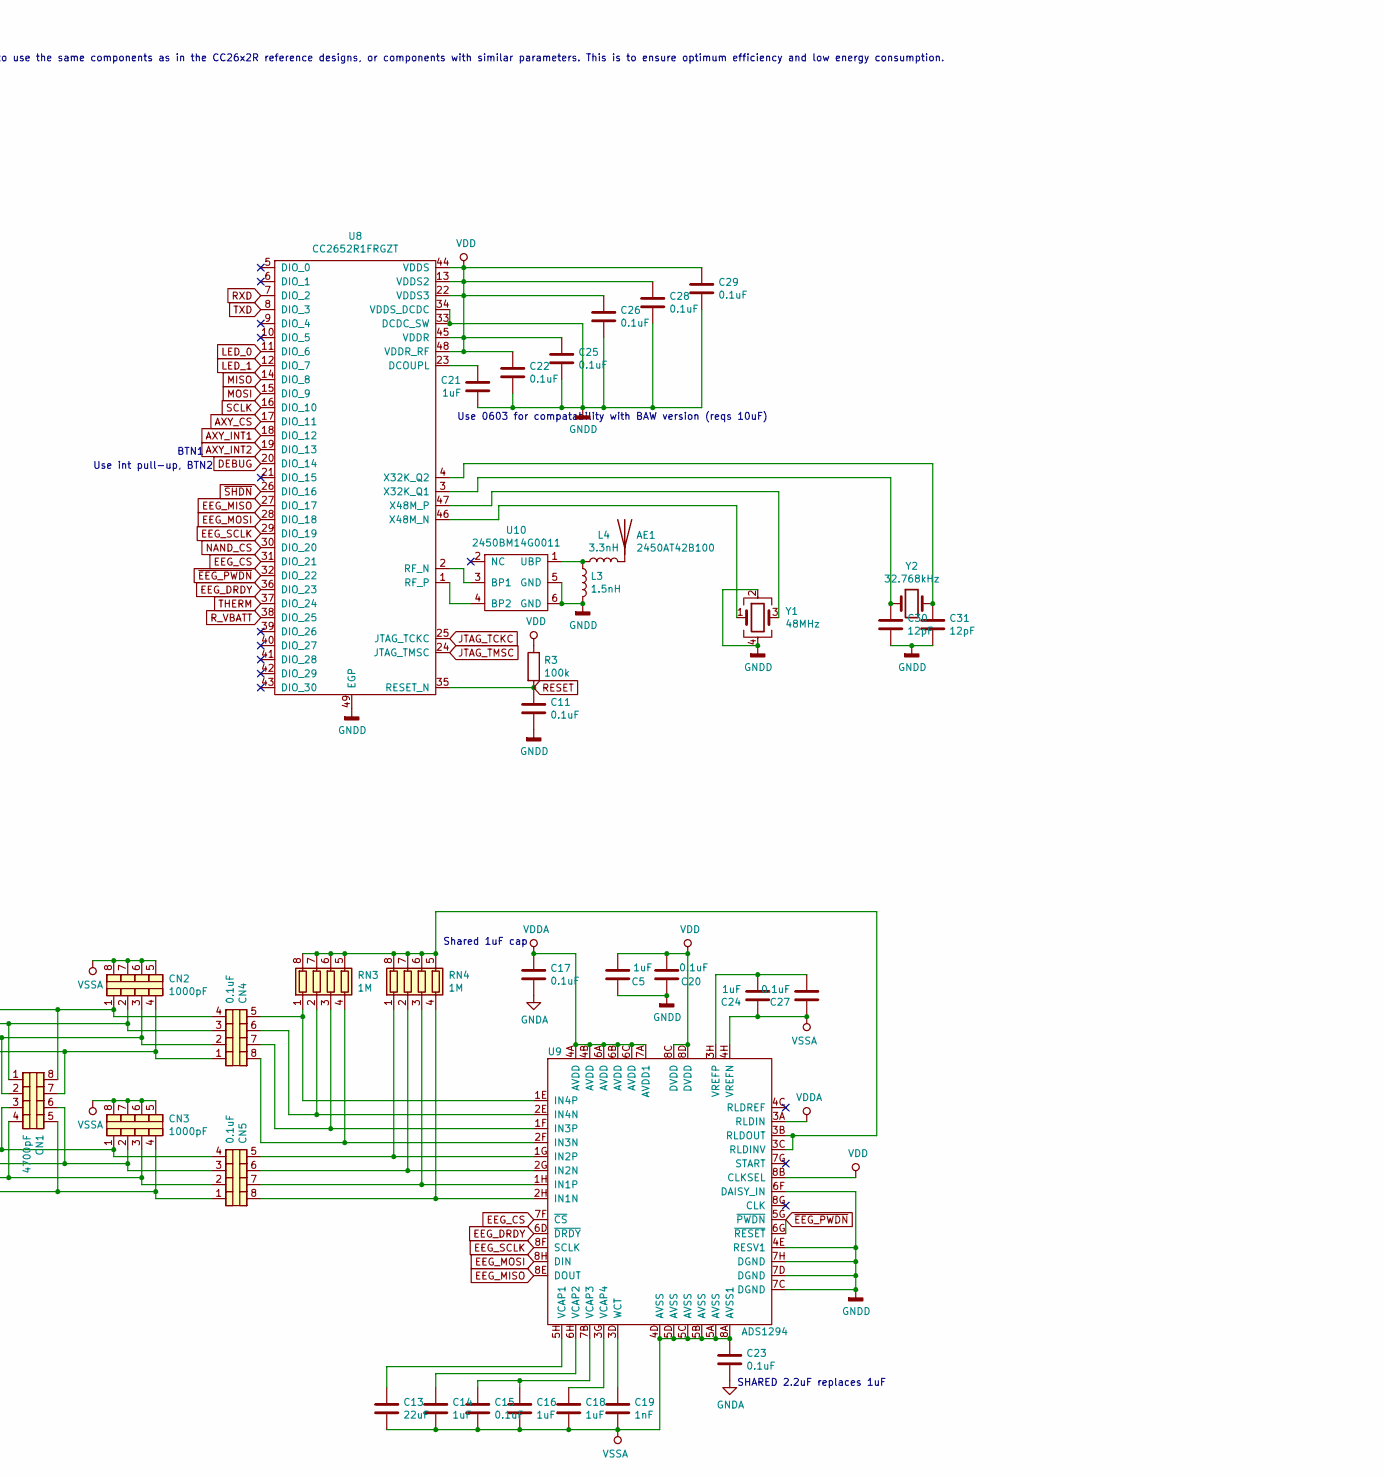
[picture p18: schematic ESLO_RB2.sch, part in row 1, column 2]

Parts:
AE1: 2450AT42B100; Digikey 712-1008-1-ND‎
C1, C2, C4: 10uF; C_0603_1608Metric; Digikey 478-8050-1-ND
C3, C5, C14, C16, C18, C24: 1uF; C_0402_1005Metric; Digikey 399-4873-1-ND
C6: 4.7uF; C_0402_1005Metric; Digikey 1276-1484-2-ND
C7, C12: 2.2uF; C_0402_1005Metric; Digikey 1253-CM05X5R225K10AHCT-ND
C10: 10nF; C_0402_1005Metric; Digikey 1276-1051-1-ND
C11, C15, C17, C20, C22, C23, C25, C26, C27, C28, C29: 0.1uF; C_0402_1005Metric; Digikey 490-6328-1-ND
C13: 22uF; C_0603_1608Metric; Digikey 490-7611-1-ND
C19: 1nF; C_0402_1005Metric; Digikey 478-1101-1-ND
C21: 1uF; C_0603_1608Metric; Digikey 399-7847-2-ND
C30, C31: 12pF; C_0402_1005Metric; Digikey 490-5924-2-ND
CN1: 4700pF; 0612_array; Digikey 399-CA064X473K4RACTUTR-ND
CN2, CN3: 1000pF; 0508_array; Digikey 399-12980-1-ND
CN4, CN5: 0.1uF; 0508_array; Digikey 478-7584-2-ND
D1: LED; LED_0402_1005Metric; Digikey VLMB1500-GS08CT-ND
D2: LED; LED_0402_1005Metric; Digikey VLMO1500-GS08CT-ND
FB1: Ferrite_Bead; C_0603_1608Metric; Digikey 490-5216-2-ND
J1: Biopotentials; ESLO_IO_8_1-27; Digikey ED8250-ND
J2: PWR/COMM; ESLO_IO_8_1-27; Digikey ED90570-ND
J3: Conn_01x02_Female; ESLO_2pin_THERM
L1: 2.2uH; L_0805_2012Metric; Digikey 490-4994-2-ND
L3: 1.5nH; L_0402_1005Metric; Digikey 334-1083-2-ND
L4: 3.3nH; L_0402_1005Metric; Digikey 712-1416-1-ND
NT1: Net-Tie_2; NetTie-2_SMD_Pad0.5mm
R1, R2, R3, R8: 100k; LED_0402_1005Metric; Digikey 311-100KLRCT-ND
R4: 21.5k; R_0402_1005Metric; Digikey RMCF0402FT21K5CT-ND
R5: 80.6k; R_0402_1005Metric; Digikey RMCF0402FT80K6CT-ND
RN1, RN2: 4.7k; 0502_array; Digikey Y6472CT-ND
RN3, RN4: 1M; 0502_array; Digikey Y6105CT-ND
TP1: TestPoint; Half2032Clip_BC-2003; Digikey 36-3036-ND
TP2: TestPoint; 5015_TP; Digikey 36-5015TR-ND
U1: MAX1720; SOT-23-6; Digikey MAX1720EUTGOSCT-ND
U2: TPS7A2015PDQNR; Texas_X2SON-4_1x1mm_P0.65mm; Digikey 296-TPS7A2015PDQNRTR-ND
U3: LSM6DSOXTR; LGA-14_3x2.5mm_P0.5mm_LayoutBorder3x4y; Digikey 497-18367-2-ND
U4: TPS62243_WSON; WSON-6-1EP_2x2mm_P0.65mm_EP1x1.6mm; Digikey 296-46476-1-ND
U6: TPS72301DRVR; WSON-6-1EP_2x2mm_P0.65mm_EP1x1.6mm; Digikey 296-TPS72301DRVRTR-ND
U7: AS5F18G04SND-10LIN; 8x6mm_WSON_UTSO; Digikey 1450-AS5F18G04SND-10LIN-ND
U8: CC2652R1FRGZT; QFN-48-1EP_7x7mm_P0.5mm_EP5.15x5.15mm; Mouser 595-CC2652R1FRGZR
U9: ADS1294; BGA-64_8x8_8.0x8.0mm_ADS129x; Digikey 296-28024-1-ND
U10: 2450BM14G0011; Digikey 712-1620-1-ND
Y1: 48MHz; Crystal_SMD_2016-4Pin_2.0x1.6mm; Digikey 535-13927-2-ND
Y2: 32.768kHz; Crystal_SMD_2012-2Pin_2.0x1.2mm; Digikey SER4081TR-ND

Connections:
+BATT: C6.1, J2.4, R1.1, TP1.1, U4.4 (EN), U4.5 (VIN)
AXY_CS: U3.12 (CS), U8.17 (DIO_11)
AXY_INT1: U3.9 (INT2), U8.18 (DIO_12)
AXY_INT2: U3.4 (INT1), U8.19 (DIO_13)
DEBUG: J2.8, U8.20 (DIO_14)
EEG_CS: U8.31 (DIO_21), U9.7F (~CS)
EEG_DRDY: U8.36 (DIO_23), U9.6D (~DRDY)
EEG_MISO: U8.27 (DIO_17), U9.8E (DOUT)
EEG_MOSI: U8.28 (DIO_18), U9.8H (DIN)
EEG_SCLK: U8.29 (DIO_19), U9.8F (SCLK)
GNDA: C3.2, C4.2, C10.1, C12.2, C17.2, C23.2, NT1.2, R5.2, U1.4 (GND), U2.2 (GND), U2.5 (THERM), U6.5 (GND)
GNDD: C1.2, C5.1, C6.2, C7.2, C11.2, C20.1, C21.1, C22.2, C25.2, C26.2, C28.2, C29.2, C30.2, C31.2, D1.1 (K), D2.1 (K), J2.5, J3.1, L3.2, NT1.1, R2.2, TP2.1, U3.2 (SDX), U3.3 (SCX), U3.6 (GND), U3.7 (GND), U4.2 (MODE), U4.6 (GND), U7.4 (Vss), U8.33 (DCDC_SW), U8.34 (VDDS_DCDC), U8.49 (EGP), U9.4E (RESV1), U9.6F (DAISY_IN), U9.7C (DGND), U9.7D (DGND), U9.7H (DGND), U10.5 (GND), U10.6 (GND), Y1.2, Y1.4
JTAG_TCKC: J2.3, U8.25 (JTAG_TCKC)
JTAG_TMSC: J2.2, U8.24 (JTAG_TMSC)
LED_0: D1.2 (A), U8.11 (DIO_6)
LED_1: D2.2 (A), U8.12 (DIO_7)
MISO: U3.1 (SDO/SA0), U7.2 (SO), U8.14 (DIO_8)
MOSI: U3.14 (SDA), U7.5 (SI), U8.15 (DIO_9)
NAND_CS: U7.1 (~CS), U8.30 (DIO_20)
unnamed: AE1.1, L4.2
unnamed: C1.1, FB1.2, L1.2, U4.3 (FB)
unnamed: C2.1, U1.6 (C1+)
unnamed: C2.2, U1.3 (C1-)
unnamed: C4.1, U1.1 (OUT), U6.6 (IN)
unnamed: C10.2, R4.2, R5.1, U6.2 (FB,NR)
unnamed: C13.1, U9.5H (VCAP1)
unnamed: C14.1, U9.6H (VCAP2)
unnamed: C15.1, C16.1, U9.7B (VCAP3)
unnamed: C18.1, U9.3G (VCAP4)
unnamed: C19.1, U9.3D (WCT)
unnamed: C21.2, U8.23 (DCOUPL)
unnamed: C24.2, C27.2, U9.3H (VREFP)
unnamed: C30.1, U8.3 (X32K_Q1), Y2.1
unnamed: C31.1, U8.4 (X32K_Q2), Y2.2
unnamed: CN1.1 (C1.1), CN2.2 (C2.1), CN4.3 (C3.1), RN1.6 (R3.2)
unnamed: CN1.2 (C2.1), CN2.3 (C3.1), CN4.2 (C2.1), RN1.7 (R2.2)
unnamed: CN1.3 (C3.1), CN3.1 (C1.1), CN5.4 (C4.1), RN2.5 (R4.2)
unnamed: CN1.4 (C4.1), CN3.3 (C3.1), CN5.2 (C2.1), RN2.7 (R2.2)
unnamed: CN1.5 (C4.2), CN3.4 (C4.1), CN5.1 (C1.1), RN2.8 (R1.2)
unnamed: CN1.6 (C3.2), CN3.2 (C2.1), CN5.3 (C3.1), RN2.6 (R3.2)
unnamed: CN1.7 (C2.2), CN2.4 (C4.1), CN4.1 (C1.1), RN1.8 (R1.2)
unnamed: CN1.8 (C1.2), CN2.1 (C1.1), CN4.4 (C4.1), RN1.5 (R4.2)
unnamed: CN4.5 (C4.2), RN3.1 (R1.1), U9.1E (IN4P)
unnamed: CN4.6 (C3.2), RN3.2 (R2.1), U9.2E (IN4N)
unnamed: CN4.7 (C2.2), RN3.3 (R3.1), U9.1F (IN3P)
unnamed: CN4.8 (C1.2), RN3.4 (R4.1), U9.2F (IN3N)
unnamed: CN5.5 (C4.2), RN4.1 (R1.1), U9.1G (IN2P)
unnamed: CN5.6 (C3.2), RN4.2 (R2.1), U9.2G (IN2N)
unnamed: CN5.7 (C2.2), RN4.3 (R3.1), U9.1H (IN1P)
unnamed: CN5.8 (C1.2), RN4.4 (R4.1), U9.2H (IN1N)
unnamed: J1.1, RN2.1 (R1.1)
unnamed: J1.2, RN2.2 (R2.1)
unnamed: J1.3, RN2.3 (R3.1)
unnamed: J1.4, RN2.4 (R4.1)
unnamed: J1.5, RN1.1 (R1.1)
unnamed: J1.6, RN1.2 (R2.1)
unnamed: J1.7, RN1.3 (R3.1)
unnamed: J1.8, RN1.4 (R4.1)
unnamed: L1.1, U4.1 (SW)
unnamed: L3.1, L4.1, U10.1 (UBP)
unnamed: RN3.5 (R4.2), RN3.6 (R3.2), RN3.7 (R2.2), RN3.8 (R1.2), RN4.5 (R4.2), RN4.6 (R3.2), RN4.7 (R2.2), RN4.8 (R1.2), U9.3B (RLDOUT), U9.3C (RLDINV)
unnamed: U8.46 (X48M_N), Y1.1
unnamed: U8.47 (X48M_P), Y1.3
unnamed: U8.2 (RF_N), U10.3 (BP1)
unnamed: U8.1 (RF_P), U10.4 (BP2)
RESET: C11.1, J2.1, R3.2, U8.35 (RESET_N)
RXD: J2.6, U8.7 (DIO_2)
R_VBATT: R1.2, R2.1, U8.38 (DIO_25)
SCLK: U3.13 (SCL), U7.6 (SCK), U8.16 (DIO_10)
THERM: J3.2, R8.2, U8.37 (DIO_24)
TXD: J2.7, U8.8 (DIO_3)
VDD: C5.2, C7.1, C20.2, C22.1, C25.1, C26.1, C28.1, C29.1, FB1.1, R3.1, R8.1, U1.2 (IN), U2.4 (IN), U3.5 (VDDIO), U3.8 (VDD), U7.3 (~WP), U7.7 (~HOLD), U7.8 (Vcc), U8.13 (VDDS2), U8.22 (VDDS3), U8.44 (VDDS), U8.45 (VDDR), U8.48 (VDDR_RF), U9.8B (CLKSEL), U9.8C (DVDD), U9.8D (DVDD)
VDDA: C3.1, C17.1, U2.1 (OUT), U9.3A (RLDIN), U9.4A (AVDD), U9.4B (AVDD), U9.6A (AVDD), U9.6B (AVDD), U9.6C (AVDD), U9.7A (AVDD1)
VSSA: C12.1, C13.2, C14.2, C15.2, C16.2, C18.2, C19.2, C23.1, C24.1, C27.1, CN2.5 (C4.2), CN2.6 (C3.2), CN2.7 (C2.2), CN2.8 (C1.2), CN3.5 (C4.2), CN3.6 (C3.2), CN3.7 (C2.2), CN3.8 (C1.2), R4.1, U6.1 (OUT), U9.4D (AVSS), U9.4H (VREFN), U9.5A (AVSS), U9.5B (AVSS), U9.5C (AVSS), U9.5D (AVSS), U9.8A (AVSS1)
~EEG_PWDN: U8.32 (DIO_22), U9.5G (~PWDN), U9.6G (~RESET)
~SHDN: U1.5 (~SHDN), U2.3 (EN), U6.4 (EN), U8.26 (DIO_16)

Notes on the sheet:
Vo=-1.186*(1+33000/63400)
(-1.5v)
(+1.5v)
(-1.8v)
SHARED TPS723 rec 2.2uF MAX1720 rec 10uF
SHARED CAP
BTN1
Shared 1uF cap
SHARED 2.2uF replaces 1uF
Use int pull-up, BTN2
LOW for DEBUG mode Use ED8250-ND 50-pos pins to interface
Needs 1.8V for level shifters
10nF = 10000pF
Tried replacing with 1M, voltage was inaccurate *200K across Vbatt = 13uA
see TPS72301DRVR 2x2 package
Hardware Migration From CC26x0 to CC26x2R 3 DCDC Regulator Components The DCDC regulator components, the output inductor and capacitor values used with the CC26x2R are updated to 6.8 μH and 22 μF, respectively. This is done to reduce the current consumption even further. It is highly recommended to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
was MT29 2Gb
use 3V LED
Shared 0.1uF (100nF) cap on EEG VDD?
Use 0603 for compatability with BAW version (reqs 10uF)
This PCB layout needs work (there’s a power pad!), see datasheet and reference design
Need to be careful about shared caps, can lead to unstable power supplies

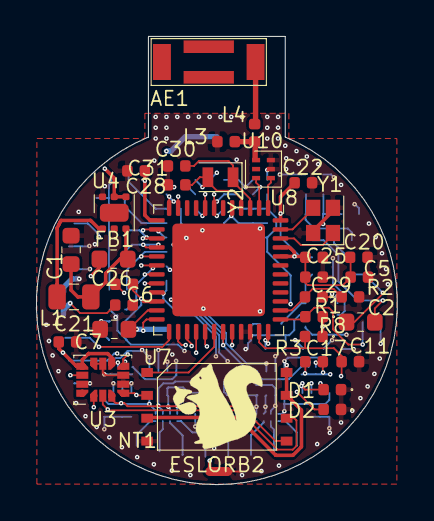
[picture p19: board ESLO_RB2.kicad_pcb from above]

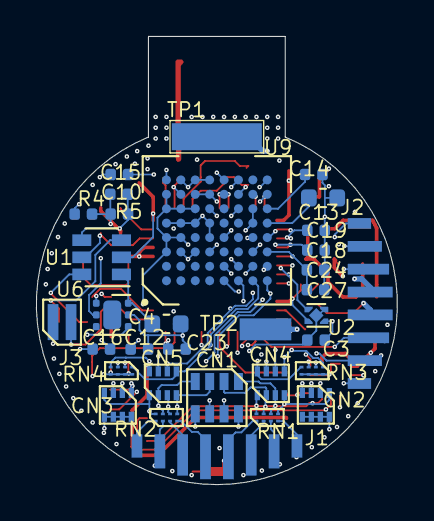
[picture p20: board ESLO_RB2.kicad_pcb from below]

Board: 4 copper layers, 20.0 x 24.9 mm, 68 parts (33 on the bottom side), 76 nets.

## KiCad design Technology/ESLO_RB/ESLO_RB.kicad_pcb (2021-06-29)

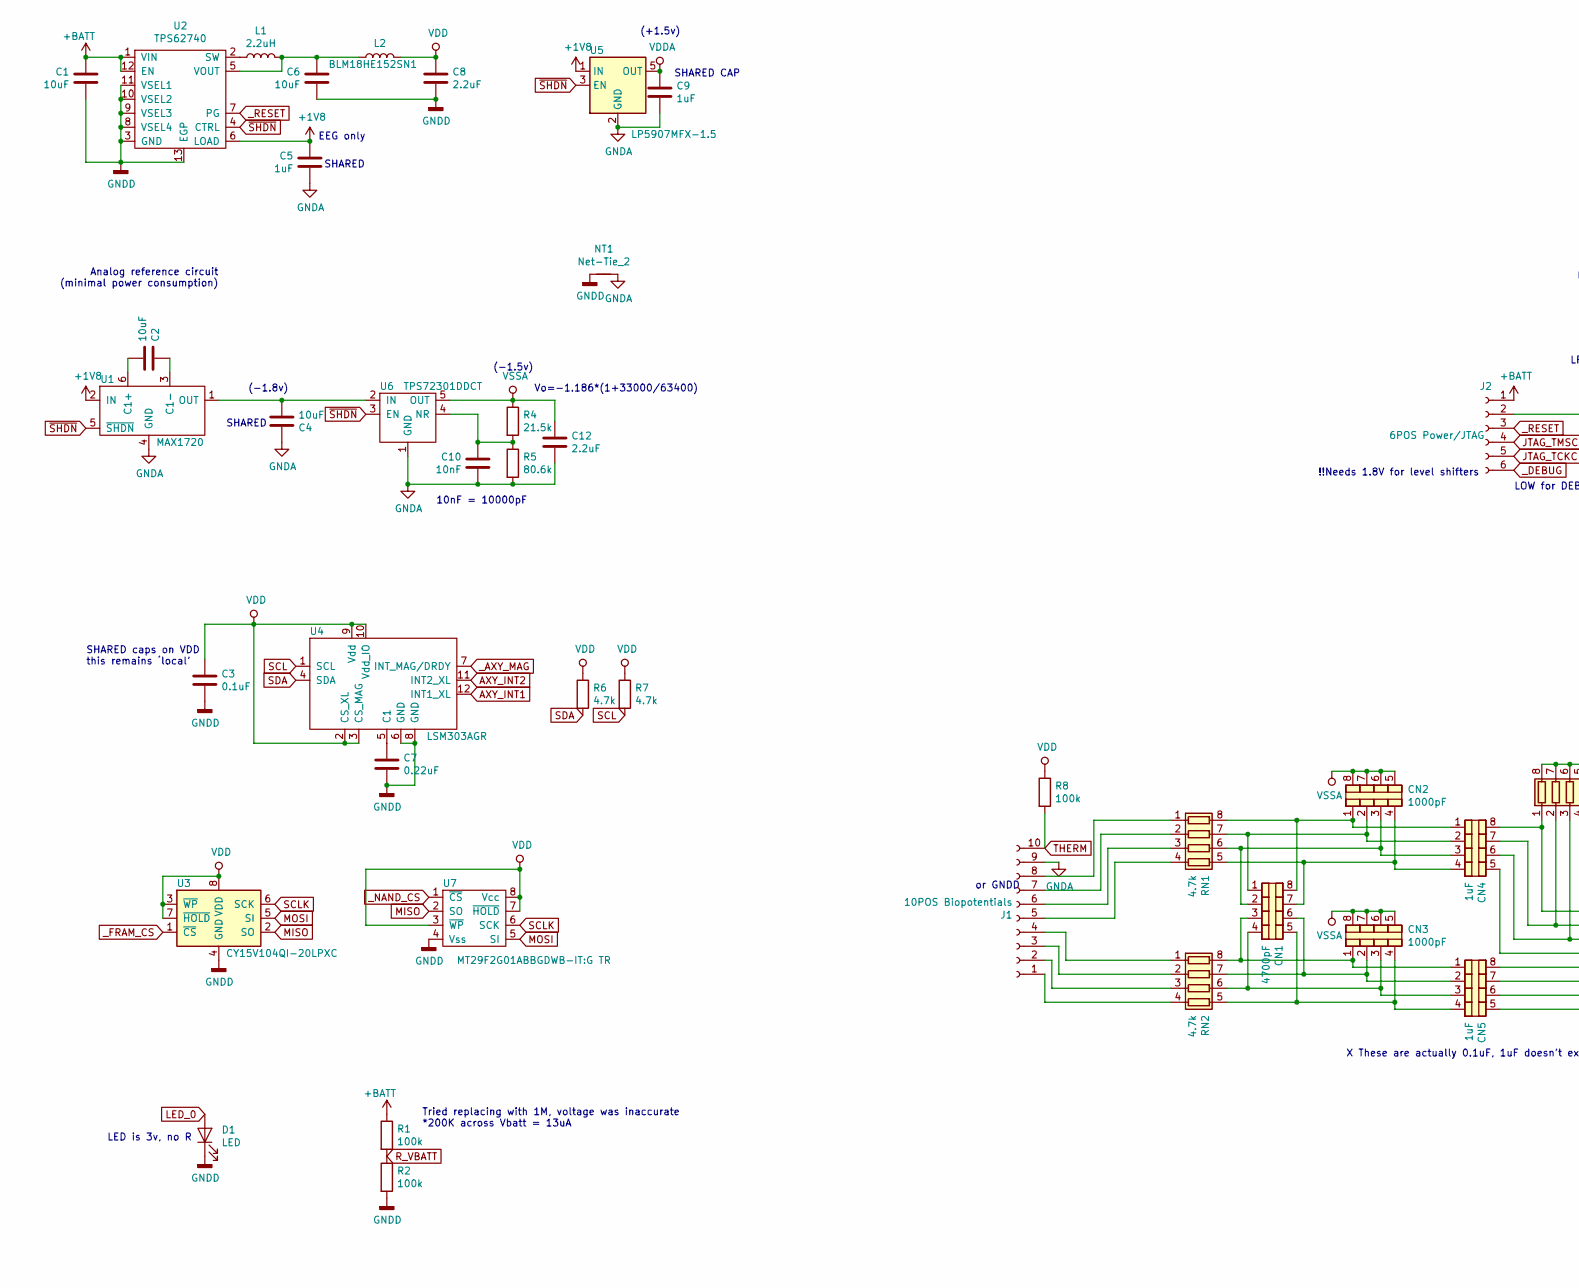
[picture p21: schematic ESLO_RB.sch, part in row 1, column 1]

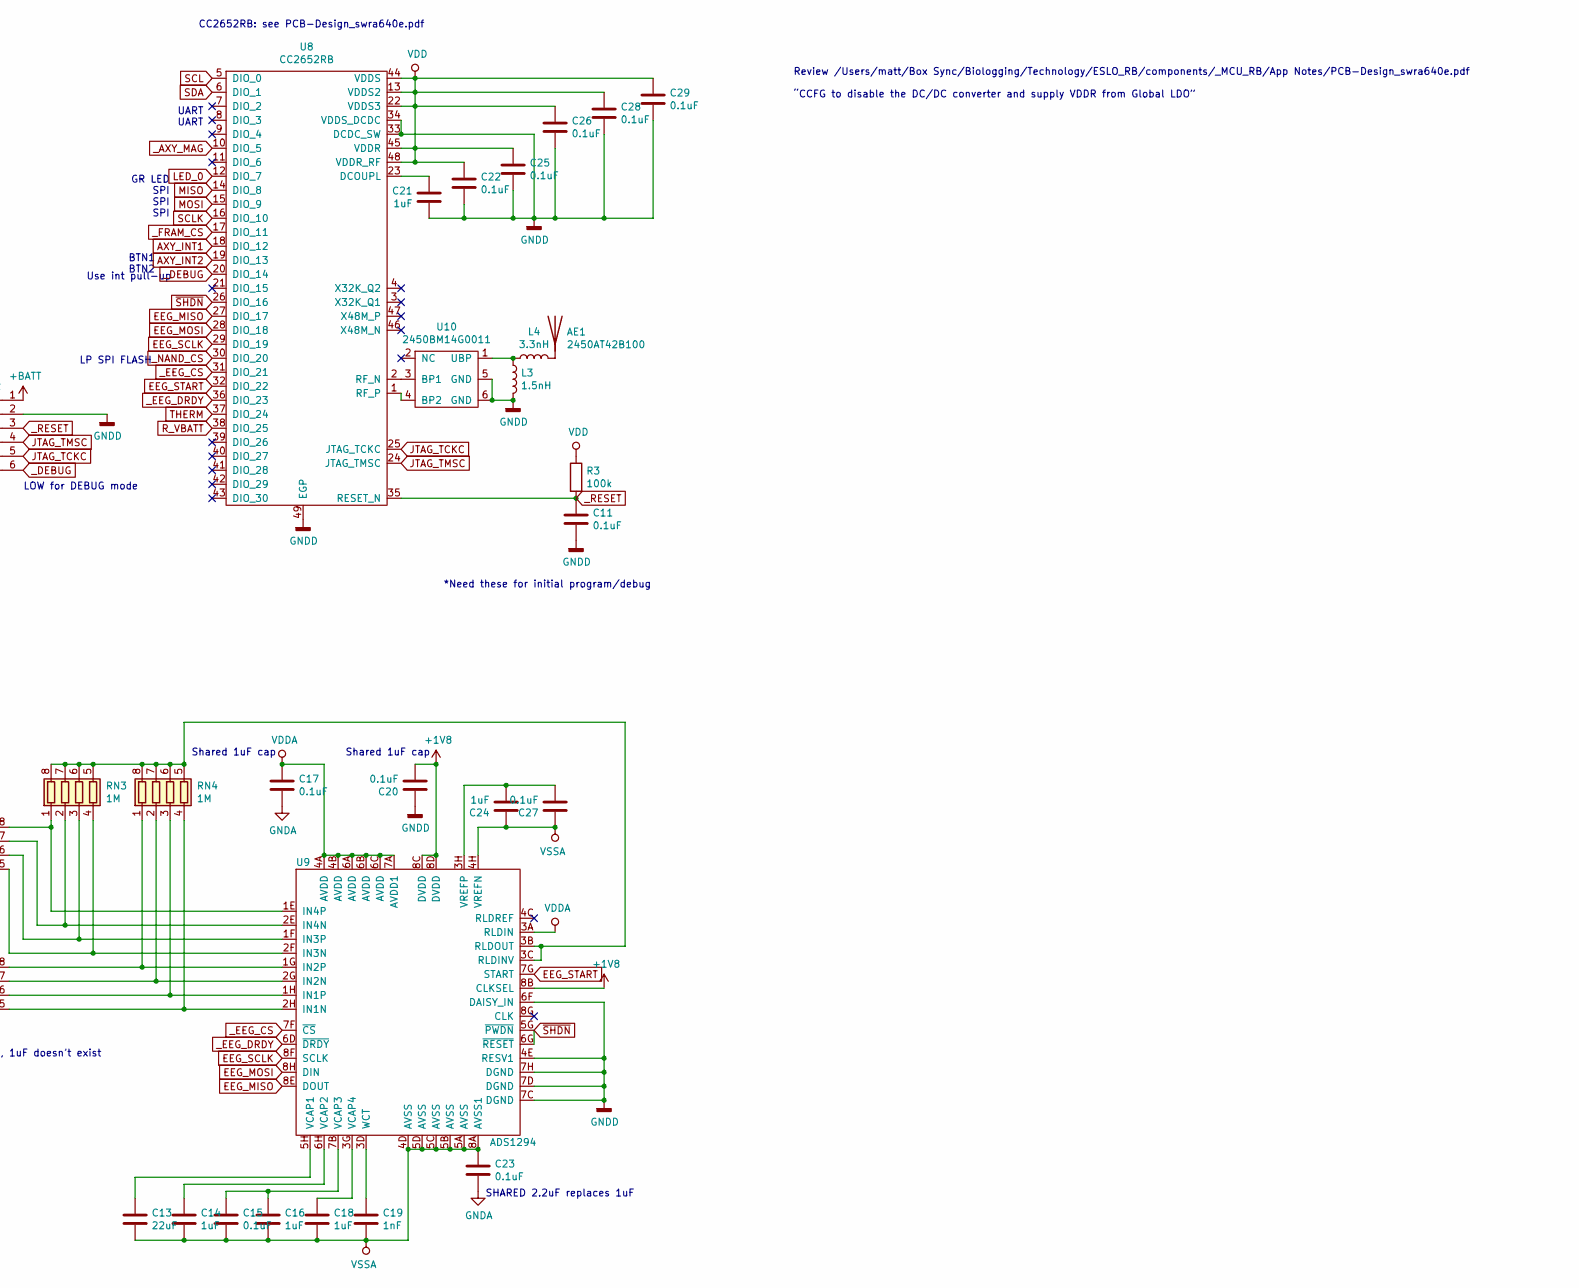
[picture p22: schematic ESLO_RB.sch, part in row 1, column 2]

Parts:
AE1: 2450AT42B100; Digikey 712-1008-1-ND‎
C1, C2, C4, C6: 10uF; C_0603_1608Metric; Digikey 490-14372-1-ND
C3, C11, C15, C17, C20, C22, C23, C25, C26, C27, C28, C29: 0.1uF; C_0402_1005Metric; Digikey 490-6328-1-ND
C5, C9, C14, C16, C18, C21, C24: 1uF; C_0402_1005Metric; Digikey 399-4873-1-ND
C7: 0.22uF; C_0402_1005Metric; Digikey 1276-1176-1-ND
C8, C12: 2.2uF; C_0402_1005Metric; Digikey 1276-1469-1-ND
C10: 10nF; C_0402_1005Metric; Digikey 1276-1051-1-ND
C13: 22uF; C_0603_1608Metric; Digikey 1276-2867-1-ND
C19: 1nF; C_0402_1005Metric; Digikey 478-1101-1-ND
CN1: 4700pF; 0508_array; Mouser 581-W2A41C472KAT2A
CN2, CN3: 1000pF; 0508_array; Digikey 478-W2A45C102KAT2ACT-ND
CN4, CN5: 1uF; 0508_array; Mouser 581-W2L16D105MAT1A
D1: LED; LED_0603_1608Metric; Digikey SML-D12V1WT86CT-ND
J1: 10POS Biopotentials; ARBO_IO10_1.27mm; Digikey ED10276-ND
J2: 6POS Power/JTAG; ARBO_IO6_1.27mm; Digikey ED10273-ND
L1: 2.2uH; L_0805_2012Metric; Digikey 490-7781-1-ND
L2: BLM18HE152SN1; L_0603_1608Metric; Digikey 490-5216-1-ND
L3: 1.5nH; L_0402_1005Metric; Digikey 712-1411-1-ND
L4: 3.3nH; L_0402_1005Metric; Digikey 712-1416-1-ND
NT1: Net-Tie_2; NetTie-2_SMD_Pad0.5mm
R1, R2, R3, R8: 100k; LED_0402_1005Metric; Digikey 311-100KLRCT-ND
R4: 21.5k; R_0402_1005Metric; Digikey RMCF0402FT21K5CT-ND
R5: 80.6k; R_0402_1005Metric; Digikey RMCF0402FT80K6CT-ND
R6, R7: 4.7k; R_0402_1005Metric; Digikey 311-4.7KJRCT-ND
RN1, RN2: 4.7k; 0502_array; Digikey Y6472CT-ND
RN3, RN4: 1M; 0502_array; Digikey Y6105CT-ND
U1: MAX1720; SOT-23-6; Digikey MAX1720EUTGOSCT-ND
U2: TPS62740; WSON-12-1EP_3x2mm_P0.5mm_EP1x2.65; Digikey 296-39459-1-ND
U3: CY15V104QI-20LPXC; 8-GQFN_FRAM_3.28mm-3.23mm; Digikey 428-4724-ND
U4: LSM303AGR; LGA-12_2x2mm_P0.5mm; Digikey 497-16527-1-ND
U5: LP5907MFX-1.5; SOT-23-5; Digikey 296-40355-1-ND
U6: TPS72301DDCT; SOT-23-5; Digikey 296-38438-1-ND
U7: MT29F2G01ABBGDWB-IT:G TR; 8x6mm_WSON_UTSO; Digikey 557-1665-1-ND
U8: CC2652RB; QFN-48-1EP_7x7mm_P0.5mm_EP5.15x5.15mm; Digikey 296-CC2652RB1FRGZRCT-ND
U9: ADS1294; BGA-64_8x8_8.0x8.0mm_ADS129x; Digikey 296-28024-1-ND
U10: 2450BM14G0011; Digikey 712-1620-1-ND

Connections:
+1V8: C5.2, C20.2, U1.2 (IN), U2.6 (LOAD), U5.1 (IN), U9.8B (CLKSEL), U9.8C (DVDD), U9.8D (DVDD)
+BATT: C1.2, J2.1, R1.1, U2.1 (VIN), U2.12 (EN)
AXY_INT1: U4.12 (INT1_XL), U8.18 (DIO_12)
AXY_INT2: U4.11 (INT2_XL), U8.19 (DIO_13)
EEG_MISO: U8.27 (DIO_17), U9.8E (DOUT)
EEG_MOSI: U8.28 (DIO_18), U9.8H (DIN)
EEG_SCLK: U8.29 (DIO_19), U9.8F (SCLK)
EEG_START: U8.32 (DIO_22), U9.7G (START)
GNDA: C4.2, C5.1, C9.2, C10.1, C12.2, C17.2, C23.2, J1.9, NT1.2, R5.2, U1.4 (GND), U5.2 (GND), U6.1 (GND)
GNDD: C1.1, C3.2, C6.1, C7.1, C8.2, C11.2, C20.1, C21.1, C22.2, C25.2, C26.2, C28.2, C29.2, D1.1 (K), J2.2, L3.2, NT1.1, R2.2, U2.3 (GND), U2.8 (VSEL4), U2.9 (VSEL3), U2.10 (VSEL2), U2.11 (VSEL1), U2.13 (EGP), U3.4 (GND), U4.6 (GND), U4.8 (GND), U7.4 (Vss), U8.33 (DCDC_SW), U8.34 (VDDS_DCDC), U8.49 (EGP), U9.4E (RESV1), U9.6F (DAISY_IN), U9.7C (DGND), U9.7D (DGND), U9.7H (DGND), U10.5 (GND), U10.6 (GND)
JTAG_TCKC: J2.5, U8.25 (JTAG_TCKC)
JTAG_TMSC: J2.4, U8.24 (JTAG_TMSC)
LED_0: D1.2 (A), U8.12 (DIO_7)
MISO: U3.2 (SO), U7.2 (SO), U8.14 (DIO_8)
MOSI: U3.5 (SI), U7.5 (SI), U8.15 (DIO_9)
unnamed: AE1.1, L4.2
unnamed: C2.1, U1.6 (C1+)
unnamed: C2.2, U1.3 (C1-)
unnamed: C4.1, U1.1 (OUT), U6.2 (IN)
unnamed: C6.2, L1.2, L2.1, U2.5 (VOUT)
unnamed: C7.2, U4.5 (C1)
unnamed: C10.2, R4.2, R5.1, U6.4 (NR)
unnamed: C13.1, U9.5H (VCAP1)
unnamed: C14.1, U9.6H (VCAP2)
unnamed: C15.1, C16.1, U9.7B (VCAP3)
unnamed: C18.1, U9.3G (VCAP4)
unnamed: C19.1, U9.3D (WCT)
unnamed: C21.2, U8.23 (DCOUPL)
unnamed: C24.2, C27.2, U9.3H (VREFP)
unnamed: CN1.1 (C1.1), CN2.2 (C2.1), CN4.2 (C2.1), RN1.7 (R2.2)
unnamed: CN1.2 (C2.1), CN2.3 (C3.1), CN4.3 (C3.1), RN1.6 (R3.2)
unnamed: CN1.3 (C3.1), CN3.1 (C1.1), CN5.1 (C1.1), RN2.8 (R1.2)
unnamed: CN1.4 (C4.1), CN3.3 (C3.1), CN5.3 (C3.1), RN2.6 (R3.2)
unnamed: CN1.5 (C4.2), CN3.4 (C4.1), CN5.4 (C4.1), RN2.5 (R4.2)
unnamed: CN1.6 (C3.2), CN3.2 (C2.1), CN5.2 (C2.1), RN2.7 (R2.2)
unnamed: CN1.7 (C2.2), CN2.4 (C4.1), CN4.4 (C4.1), RN1.5 (R4.2)
unnamed: CN1.8 (C1.2), CN2.1 (C1.1), CN4.1 (C1.1), RN1.8 (R1.2)
unnamed: CN4.5 (C4.2), RN3.4 (R4.1), U9.2F (IN3N)
unnamed: CN4.6 (C3.2), RN3.3 (R3.1), U9.1F (IN3P)
unnamed: CN4.7 (C2.2), RN3.2 (R2.1), U9.2E (IN4N)
unnamed: CN4.8 (C1.2), RN3.1 (R1.1), U9.1E (IN4P)
unnamed: CN5.5 (C4.2), RN4.4 (R4.1), U9.2H (IN1N)
unnamed: CN5.6 (C3.2), RN4.3 (R3.1), U9.1H (IN1P)
unnamed: CN5.7 (C2.2), RN4.2 (R2.1), U9.2G (IN2N)
unnamed: CN5.8 (C1.2), RN4.1 (R1.1), U9.1G (IN2P)
unnamed: J1.1, RN2.4 (R4.1)
unnamed: J1.2, RN2.3 (R3.1)
unnamed: J1.3, RN2.2 (R2.1)
unnamed: J1.4, RN2.1 (R1.1)
unnamed: J1.5, RN1.4 (R4.1)
unnamed: J1.6, RN1.3 (R3.1)
unnamed: J1.7, RN1.2 (R2.1)
unnamed: J1.8, RN1.1 (R1.1)
unnamed: L1.1, U2.2 (SW)
unnamed: L3.1, L4.1, U10.1 (UBP)
unnamed: RN3.5 (R4.2), RN3.6 (R3.2), RN3.7 (R2.2), RN3.8 (R1.2), RN4.5 (R4.2), RN4.6 (R3.2), RN4.7 (R2.2), RN4.8 (R1.2), U9.3B (RLDOUT), U9.3C (RLDINV)
unnamed: U8.2 (RF_N), U10.3 (BP1)
unnamed: U8.1 (RF_P), U10.4 (BP2)
R_VBATT: R1.2, R2.1, U8.38 (DIO_25)
SCL: R7.2, U4.1 (SCL), U8.5 (DIO_0)
SCLK: U3.6 (SCK), U7.6 (SCK), U8.16 (DIO_10)
SDA: R6.2, U4.4 (SDA), U8.6 (DIO_1)
THERM: J1.10, R8.2, U8.37 (DIO_24)
VDD: C3.1, C8.1, C22.1, C25.1, C26.1, C28.1, C29.1, L2.2, R3.1, R6.1, R7.1, R8.1, U3.3 (~WP), U3.7 (~HOLD), U3.8 (VDD), U4.2 (CS_XL), U4.3 (CS_MAG), U4.9 (Vdd), U4.10 (Vdd_IO), U7.3 (~WP), U7.7 (~HOLD), U7.8 (Vcc), U8.13 (VDDS2), U8.22 (VDDS3), U8.44 (VDDS), U8.45 (VDDR), U8.48 (VDDR_RF)
VDDA: C9.1, C17.1, U5.5 (OUT), U9.3A (RLDIN), U9.4A (AVDD), U9.4B (AVDD), U9.6A (AVDD), U9.6B (AVDD), U9.6C (AVDD), U9.7A (AVDD1)
VSSA: C12.1, C13.2, C14.2, C15.2, C16.2, C18.2, C19.2, C23.1, C24.1, C27.1, CN2.5 (C4.2), CN2.6 (C3.2), CN2.7 (C2.2), CN2.8 (C1.2), CN3.5 (C4.2), CN3.6 (C3.2), CN3.7 (C2.2), CN3.8 (C1.2), R4.1, U6.5 (OUT), U9.4D (AVSS), U9.4H (VREFN), U9.5A (AVSS), U9.5B (AVSS), U9.5C (AVSS), U9.5D (AVSS), U9.8A (AVSS1)
_AXY_MAG: U4.7 (INT_MAG/DRDY), U8.10 (DIO_5)
_DEBUG: J2.6, U8.20 (DIO_14)
_EEG_CS: U8.31 (DIO_21), U9.7F (~CS)
_EEG_DRDY: U8.36 (DIO_23), U9.6D (~DRDY)
_FRAM_CS: U3.1 (~CS), U8.17 (DIO_11)
_NAND_CS: U7.1 (~CS), U8.30 (DIO_20)
_RESET: C11.1, J2.3, R3.2, U2.7 (PG), U8.35 (RESET_N)
~SHDN: U1.5 (~SHDN), U2.4 (CTRL), U5.3 (EN), U6.3 (EN), U8.26 (DIO_16), U9.5G (~PWDN), U9.6G (~RESET)

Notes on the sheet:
Vo=-1.186*(1+33000/63400)
(-1.5v)
(+1.5v)
(-1.8v)
Analog reference circuit (minimal power consumption)
EEG only
Review /Users/matt/Box Sync/Biologging/Technology/ESLO_RB/components/_MCU_RB/App Notes/PCB-Design_swra640e.pdf “CCFG to disable the DC/DC converter and supply VDDR from Global LDO”
CC2652RB: see PCB-Design_swra640e.pdf
LP SPI FLASH
SHARED
SHARED CAP
BTN1 BTN2
Shared 1uF cap
SHARED 2.2uF replaces 1uF
SHARED caps on VDD this remains ‘local’
LED is 3v, no R
or GNDD
Use int pull-up
LOW for DEBUG mode
!!Needs 1.8V for level shifters
10nF = 10000pF
GR LED SPI SPI SPI
*Need these for initial program/debug
UART UART
X These are actually 0.1uF, 1uF doesn’t exist
Tried replacing with 1M, voltage was inaccurate *200K across Vbatt = 13uA

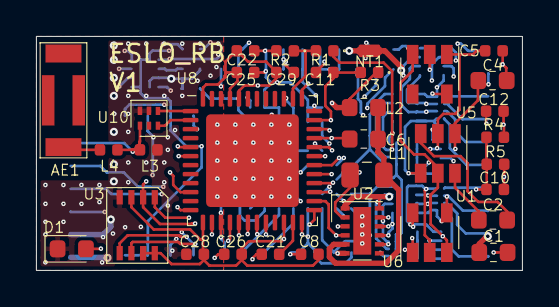
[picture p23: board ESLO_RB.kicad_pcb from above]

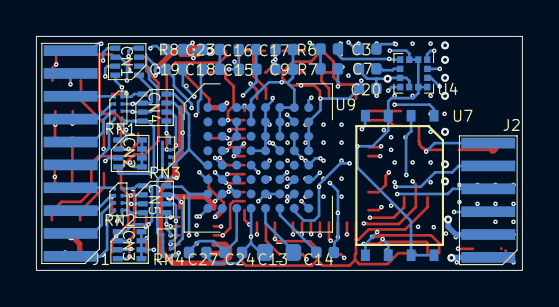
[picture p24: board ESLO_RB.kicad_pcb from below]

Board: 4 copper layers, 27.0 x 13.0 mm, 65 parts (31 on the bottom side), 74 nets.

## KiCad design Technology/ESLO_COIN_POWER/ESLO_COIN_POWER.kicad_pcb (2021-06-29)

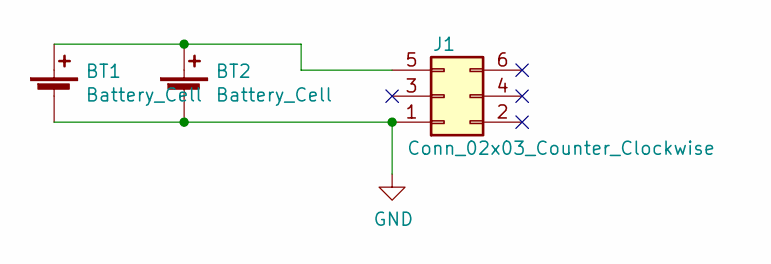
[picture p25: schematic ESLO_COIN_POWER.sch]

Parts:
BT1, BT2: Battery_Cell; BatteryHolder_Keystone_1060_1x2032; Digikey 36-1060-ND
J1: Conn_02x03_Counter_Clockwise; PinSocket_2x03_P2.54mm_Vertical; Digikey A106656-ND

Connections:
GND: BT1.2 (-), BT2.2 (-), J1.1
unnamed: BT1.1 (+), BT2.1 (+), J1.5

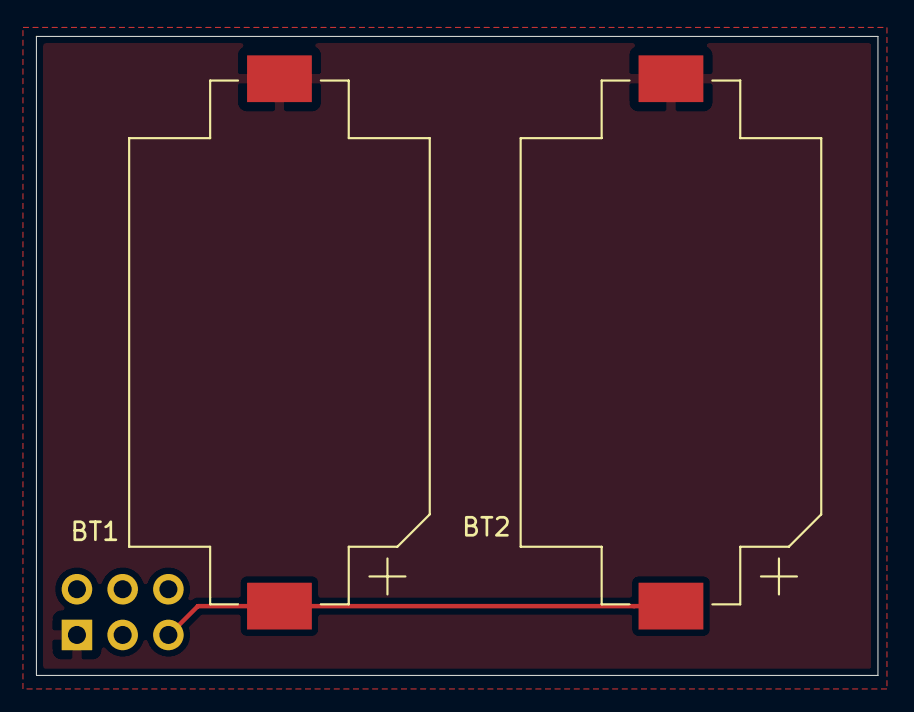
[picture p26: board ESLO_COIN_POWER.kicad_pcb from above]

Board: 2 copper layers, 46.8 x 35.5 mm, 3 parts (1 on the bottom side), 2 nets.

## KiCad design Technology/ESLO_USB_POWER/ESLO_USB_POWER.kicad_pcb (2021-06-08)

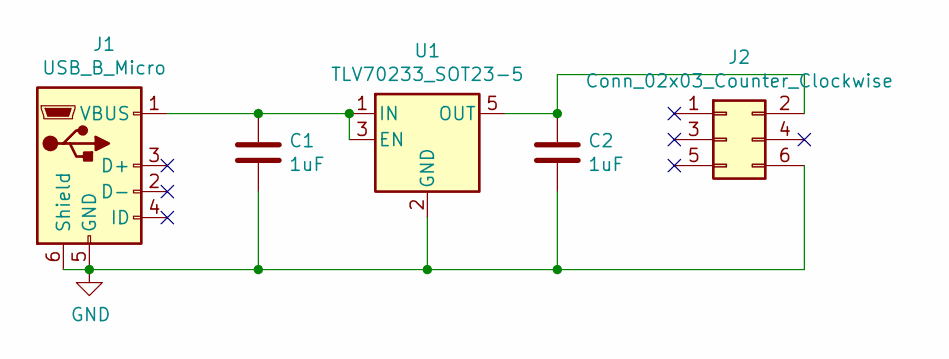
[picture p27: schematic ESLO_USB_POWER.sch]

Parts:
C1, C2: 1uF; C_0603_1608Metric; Digikey 399-11133-2-ND
J1: USB_B_Micro; USB_Micro-B_Molex-105017-0001; Digikey WM11262TR-ND
J2: Conn_02x03_Counter_Clockwise; PinSocket_2x03_P2.54mm_Vertical; Digikey A106656-ND
U1: TLV70233_SOT23-5; SOT-23-5; Digikey 296-39284-2-ND

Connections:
GND: C1.2, C2.2, J1.5 (GND), J1.6 (Shield), J2.6, U1.2 (GND)
unnamed: C1.1, J1.1 (VBUS), U1.1 (IN), U1.3 (EN)
unnamed: C2.1, J2.2, U1.5 (OUT)

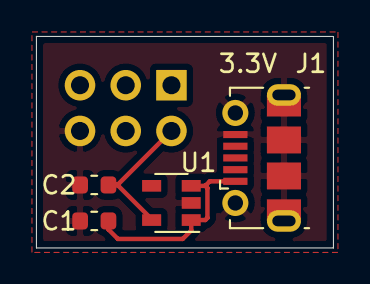
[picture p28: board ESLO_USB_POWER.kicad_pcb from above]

Board: 2 copper layers, 16.5 x 11.8 mm, 5 parts (1 on the bottom side), 3 nets.

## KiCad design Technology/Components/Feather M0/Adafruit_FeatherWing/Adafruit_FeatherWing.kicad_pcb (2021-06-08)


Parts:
AE1: 4.7uH; PA6512-AED
C1, C2, C3, C7, C8, C12, C14, C21, C23, C24, C26, C27, C32: 1uF; C_0603_1608Metric; Digikey# 1276-1102-1-ND
C4, C5: 10pF; C_0603_1608Metric; Digikey# 399-7815-1-ND
C6, C15, C35: 1000pF; C_0603_1608Metric; Digikey# 1276-1091-1-ND
C9, C22, C25, C28, C30, C33, C34, C36, C39, C40: 0.1uF; C_0603_1608Metric; Digikey# 399-1095-1-ND
C10, C11, C13: 10uF; C_0603_1608Metric; Digikey# 490-14372-1-ND
C16, C17, C18, C19: 4.7pF; C_0603_1608Metric; Digikey# 1276-1098-1-ND
C20: 100uF; C_1210_3225Metric; Digikey# 587-1388-1-ND
C29: 10uF; C_0805_2012Metric; Digikey# 1276-6456-1-ND
C31: 1.5nF; C_0805_2012Metric; Digikey# 399-16647-1-ND
C37, C38: 0.01uF; C_0603_1608Metric; Digikey# 399-17960-1-ND
D1: BLUE; LED_0603_1608Metric; Digikey# 160-1827-1-ND
D2: GREEN; LED_0603_1608Metric; Digikey# 160-1446-1-ND
D3: RED; LED_0603_1608Metric; Digikey# 160-1436-1-ND
J1: ECoG_CONN; ARBO_IO6
J2: ECG_CONN; ARBO_IO6
J3: Conn_01x02_Female; ARBO_THERM2
JP1: PinHeader_01x16_2.54mm; Conn_PinHeader_1x16; Digikey# 952-3304-ND
JP3: PinHeader_01x12_2.54mm; Conn_PinHeader_1x12; Digikey# 952-3302-ND
R1, R2: 49.9k; R_0603_1608Metric; Digikey# 311-49.9KHRCT-ND
R3: 0; R_0603_1608Metric; Digikey# 1276-3510-1-ND
R4: 499K; R_0603_1608Metric; Digikey# 541-3001-1-ND
R5, R6, R7, R8, R9, R11: 4.99k; R_0603_1608Metric; Digikey# 311-4.99KHRCT-ND
R10: 1M; R_0603_1608Metric; Digikey# 311-1.00MHRCT-ND
R12, R13, R16, R17, R18, R19: 10k; R_0603_1608Metric; Digikey# RNCP0603FTD10K0CT-ND
R14, R21, R22: 220; R_0603_1608Metric; Digikey# A130087CT-ND
R15, R20: 100; R_0603_1608Metric; Digikey# A102200CT-ND
U1: MAX30003; QFN-28-1EP_5x5mm_P0.5mm_EP3.35x3.35mm; Digikey# MAX30003CTI+TCT-ND
U2: MAX1726EUK18+; SOT-23-5; Digikey# MAX1726EUK18+T-ND
U3: MAX828; SOT-23-5; Digikey# MAX828EUK+TCT-ND
U4: ADS1299; TQFP-64_10x10mm_P0.5mm; Digikey# 296-45228-1-ND
U5: M24LR04E; TSSOP-8_4.4x3mm_P0.65mm; Digikey# 497-12878-1-ND
U6: MPU-9250; InvenSense_QFN-24_3x3mm_P0.4mm; Digikey# 1428-1019-1-ND
U7: MAX31856; TSSOP-14_4.4x5mm_P0.65mm; Digikey# MAX31856MUD+-ND

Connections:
/(DGND): JP1.13
/A0: JP1.12, U4.39 (~CS)
/A1: JP1.11, U4.47 (~DRDY)
/A2: JP1.10, R12.2, U4.35 (~PWDN)
/A3: JP1.9, R13.2, U4.36 (~RESET)
/A4: JP1.8, U6.12 (INT)
/A5: JP1.7, R14.1
/AREF: JP1.14
/D0: JP1.3
/D1: JP1.2
/D5: JP3.10, U7.9 (~CS)
/D6: JP3.9, U5.7 (RF_BUSY)
/D9: JP3.8
/D10: JP3.7, U2.5 (~SHDN)
/D11: JP3.6, U1.14 (FCLK)
/D12: JP3.5, U1.15 (CSB)
/D13: JP3.4
/ECGN: J2.6, R2.2
/ECGP: J2.5, R1.2
/ELECT_BIAS: J1.1, R11.2
/ELECT_REF: J1.6, R9.2
/EN: JP3.2
/IN1P: J1.5, R5.2
/IN2P: J1.4, R6.2
/IN3P: J1.3, R7.2
/IN4P: J1.2, R8.2
/MISO: JP1.4, U1.18 (SDO), U4.43 (DOUT), U7.11 (SDO)
/MOSI: JP1.5, U1.17 (SDI), U4.34 (DIN), U7.12 (SDI)
/SCI: JP3.11, U5.6 (SCL), U6.23 (SCL/SCLK)
/SCK: JP1.6, U1.16 (SCLK), U4.40 (SCLK), U7.10 (SCK)
/SDA: JP3.12, U5.5 (SDA), U6.24 (SDA/MOSI)
/SLV: J2.4, R4.2
/VUSB: JP3.3
/~RESET: JP1.16
GNDA: C3.1, C4.2, C5.2, C7.2, C9.2, C10.2, C12.2, C13.2, C15.2, C20.2, C21.2, C22.2, C23.2, C24.2, C25.2, C26.2, C27.1, C28.1, C29.1, C30.1, D2.1 (K), J2.1, J2.2, J2.3, R4.1, U1.1 (I.C.), U1.2 (I.C.), U1.3 (AGND), U1.4 (I.C.), U1.5 (I.C.), U1.8 (AGND), U1.24 (I.C.), U1.26 (I.C.), U1.28 (AGND), U1.29 (CASE), U3.1 (OUT), U4.20 (AVSS), U4.23 (AVSS), U4.25 (VREFN), U4.32 (AVSS), U4.53 (AVSS1), U4.57 (AVSS), U4.58 (AVSS)
GNDD: C1.2, C3.2, C11.2, C14.2, C27.2, C28.2, C32.2, C33.2, C34.2, C35.2, C36.2, C37.2, C38.2, C40.2, D1.1 (K), D3.1 (K), JP1.1, R16.1, R17.1, R18.1, R19.1, U1.12 (DGND), U2.2 (GND), U2.4 (GND), U3.4 (GND), U4.31 (RESV1), U4.33 (DGND), U4.41 (DAISY_IN), U4.49 (DGND), U4.51 (DGND), U5.4 (VSS), U6.11 (FSYNC), U6.18 (GND), U6.20 (RESV_GND), U7.1 (AGND), U7.14 (DGND)
unnamed: AE1.1, U5.3 (AC1)
unnamed: AE1.2, U5.2 (AC0)
unnamed: C2.1, U3.5 (C+)
unnamed: C2.2, U3.3 (C-)
unnamed: C4.1, C6.1, R1.1, U1.6 (ECGP)
unnamed: C5.1, C6.2, R2.1, U1.7 (ECGN)
unnamed: C8.1, U1.9 (CAPP)
unnamed: C8.2, U1.10 (CAPN)
unnamed: C10.1, U1.25 (VCM)
unnamed: C12.1, U1.27 (VBG)
unnamed: C13.1, U1.23 (VREF)
unnamed: C15.1, U1.11 (CPLL)
unnamed: C16.1, R5.1, U4.16 (IN1P)
unnamed: C16.2, C17.2, C18.2, C19.2, R9.1, U4.17 (SRB1)
unnamed: C17.1, R6.1, U4.14 (IN2P)
unnamed: C18.1, R7.1, U4.12 (IN3P)
unnamed: C19.1, R8.1, U4.10 (IN4P)
unnamed: C20.1, U4.28 (VCAP1)
unnamed: C21.1, U4.30 (VCAP2)
unnamed: C22.1, C24.1, U4.55 (VCAP3)
unnamed: C26.1, U4.26 (VCAP4)
unnamed: C29.2, C30.2, U4.24 (VREFP)
unnamed: C31.1, R10.1, U4.61 (BIASINV)
unnamed: C31.2, R10.2, R11.1, U4.63 (BIASOUT)
unnamed: C36.1, U6.10 (REGOUT)
unnamed: C37.1, C39.2, R20.1, U7.3 (T-)
unnamed: C38.1, C39.1, R15.1, U7.4 (T+)
unnamed: D1.2 (A), R14.2
unnamed: D2.2 (A), R21.2
unnamed: D3.2 (A), R22.2
unnamed: J3.1, R20.2, U7.2 (BIAS)
unnamed: J3.2, R15.2
unnamed: R3.2, U1.22 (AVDD)
unnamed: R16.2, U4.42 (GPIO1)
unnamed: R17.2, U4.44 (GPIO2)
unnamed: R18.2, U4.45 (GPIO3)
unnamed: R19.2, U4.46 (GPIO4)
VCC: U4.52 (CLKSEL)
VDC: JP3.1, U2.1 (IN)
VDD: C11.1, C32.1, C33.1, C34.1, C35.1, C40.1, JP1.15, R12.1, R13.1, R22.1, U1.19 (OVDD), U4.48 (DVDD), U4.50 (DVDD), U5.8 (VCC), U6.1 (RESV_VDDIO), U6.8 (VDDIO), U6.9 (AD0/MISO), U6.13 (VDD), U6.22 (~CS), U7.5 (AVDD), U7.8 (DVDD)
VDDA: C1.1, C7.1, C9.1, C14.1, C23.1, C25.1, R3.1, R21.1, U1.13 (DVDD), U2.3 (OUT), U3.2 (IN), U4.19 (AVDD), U4.21 (AVDD), U4.22 (AVDD), U4.54 (AVDD1), U4.56 (AVDD), U4.59 (AVDD)

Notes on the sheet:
Adalogger
ECG
Power
*Use tantalum or class 1
VDC = VBAT VDD = +3.3v VDDA = +1.8v GND = Digital GND GNDA = -1.8v, Analog GND
(unused?)
ECoG
NFC
LEDs
I/O
ACCEL
THERM



Board: 4 copper layers, 50.8 x 22.9 mm, 78 parts (26 on the bottom side), 67 nets.

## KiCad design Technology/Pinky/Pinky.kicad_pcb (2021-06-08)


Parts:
AE1, AE2: Antenna; Linx_Ant_Screw; Digikey ANT-315-PW-LP-ND
C1: 680pF; C_0402_1005Metric; Digikey 399-1027-1-ND
C2: 220pF; C_0402_1005Metric; Digikey 490-6220-1-ND
C3, C5: 15pF; C_0402_1005Metric; Digikey 399-8947-1-ND
C4: 22pF; C_0402_1005Metric; Digikey 490-5868-1-ND
C6: 1.8pF; C_0603_1608Metric; Digikey 490-9667-2-ND
C7: .039uF; C_0603_1608Metric; Digikey 311-4072-1-ND
C8, C10: 2.2uF; C_0603_1608Metric; Digikey 399-7886-1-ND
C9: 1uF; C_0603_1608Metric; Digikey 1276-1182-1-ND
D1: +3.3V; D_0603_1608Metric; Digikey 732-4971-1-ND
D2: +5V; D_0603_1608Metric; Digikey 732-4971-1-ND
D3: -6V; D_0603_1608Metric; Digikey 732-4971-1-ND
D4: +6V; D_0603_1608Metric; Digikey 732-4971-1-ND
D5: PINK_EN; D_0603_1608Metric; Digikey 732-4978-1-ND
J1: TX CONN; PinHeader_1x04_P2.54mm_Vertical
J2: SPI CONN; TerminalBlock_4Ucon_1x04_P3.50mm_Horizontal; Digikey 277-1860-ND
J3: 6V BATT; TerminalBlock_4Ucon_1x04_P3.50mm_Horizontal; Digikey 277-1860-ND
J4: SPEAKER; TerminalBlock_4Ucon_1x02_P3.50mm_Horizontal; Digikey 277-1860-ND
L1: 22nH; L_0402_1005Metric; Digikey 712-1455-1-ND
L2: 27nH; L_0402_1005Metric; Digikey 712-1413-1-ND
L3: 56nH; L_0603_1608Metric; Digikey 712-1443-1-ND
R1: 0; R_0402_1005Metric; Digikey 1276-3480-1-ND
R2, R3, R4, R6, R8: 2.2k; R_0603_1608Metric; Digikey P2.2KGCT-ND
R5, R7: 4.7k; R_0603_1608Metric; Digikey RR08P4.7KDCT-ND
RV1: 5k; Potentiometer_Bourns_3314J_Vertical; Digikey ST4ETA502CT-ND
TP1: TP_GND; TestPoint_Loop_D2.50mm_Drill1.0mm; Digikey 36-5002-ND
U1: MAX1472; SOT-23-8; Digikey MAX1472AKA+TCT-ND
U2: MICRF007; SOIC-8_3.9x4.9mm_P1.27mm; Digikey 576-1334-ND
U3: MCP9808_MSOP; MSOP-8_3x3mm_P0.65mm; Digikey MCP9808T-E/MSCT-ND
U4: Adalogger; Adafruit_feather; Digikey 1528-1539-ND
U5: VEML7700; Digikey VEML7700CT-ND
U6: NOISE2; DIP-8_W7.62mm; Digikey AE9986-ND
U7: AP2204K-5.0; SOT-23-5; Digikey AP2204K-5.0TRG1DICT-ND
U8: SN74LVC; SOT-353_SC-70-5; Digikey 296-13254-1-ND
U9: TL071; SOIC-8_3.9x4.9mm_P1.27mm; Digikey 296-14994-1-ND
Y1: 9.84375MHz; Crystal_SMD_Abracon_ABM3-2Pin_5.0x3.2mm; Digikey 535-13417-1-ND
Y2: 4.8970MHz; Crystal_SMD_HC49-SD; Digikey 535-9688-1-ND

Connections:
+3V3: J1.4, R2.1, R5.1, R7.1, RV1.1, U1.7 (VDD), U3.8 (VDD), U4.2 (3V3), U5.2 (VDD)
+5V: C10.1, R3.1, U2.3 (VDD), U4.28 (VBAT), U6.1 (5V), U7.5 (VOUT), U8.5 (VCC)
+6V: C9.1, J3.4, R6.1, U7.1 (VIN), U7.3 (EN), U9.7 (V+)
-6V: D3.2 (A), J3.1, U9.4 (V-)
GND: C1.1, C2.1, C3.1, C4.1, C7.1, C8.1, C9.2, C10.2, D1.2 (A), D2.2 (A), D4.2 (A), D5.2 (A), J1.1, J2.1, J3.2, J3.3, J4.2, L3.1, R4.1, TP1.1, U1.2 (GND), U1.3 (PAGND), U2.1 (VSS), U3.4 (GND), U3.5 (A2), U3.6 (A1), U3.7 (A0), U4.4 (GND), U4.16 (GND), U5.3 (GND), U6.8 (0V), U7.2 (GND), U8.3 (GND), Y2.2
unnamed: AE1.1, R1.2
unnamed: AE2.1, C6.1
unnamed: C1.2, C2.2, L2.2, RV1.2, RV1.3
unnamed: C3.2, L1.1, R1.1
unnamed: C4.2, C5.2, L1.2
unnamed: C5.1, L2.1, U1.4 (PAOUT)
unnamed: C6.2, L3.2, U2.2 (ANT)
unnamed: C7.2, U2.4 (CTH)
unnamed: C8.2, U2.7 (CAGC)
unnamed: D1.1 (K), R2.2
unnamed: D2.1 (K), R3.2
unnamed: D3.1 (K), R4.2
unnamed: D4.1 (K), R6.2
unnamed: D5.1 (K), R8.2
unnamed: J1.2, U1.5 (ENABLE), U4.5 (A0)
unnamed: J1.3, U1.6 (DATA), U4.6 (A1)
unnamed: J2.2, U4.13 (MISO)
unnamed: J2.3, U4.12 (MOSI)
unnamed: J2.4, U4.11 (SCK)
unnamed: J4.1, U9.2 (-), U9.6
unnamed: R8.1, U4.22 (~10), U8.4 (C)
unnamed: U1.1 (XTAL1), Y1.1
unnamed: U1.8 (XTAL2), Y1.2
unnamed: U2.5 (DO), U4.24 (12)
unnamed: U2.6 (SHUT), U4.23 (11)
unnamed: U2.8 (REFOSC), Y2.1
unnamed: U6.7 (PINK), U8.1 (A)
unnamed: U8.2 (B), U9.3 (+)
SCL: R5.2, U3.2 (SCL), U4.18 (SCL), U5.1 (SCL)
SDA: R7.2, U3.1 (SDA), U4.17 (SDA), U5.4 (SDA)


Board: 2 copper layers, 56.4 x 59.9 mm, 45 parts (0 on the bottom side), 35 nets.

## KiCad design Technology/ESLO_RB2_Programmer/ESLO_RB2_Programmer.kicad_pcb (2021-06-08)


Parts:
1.8V1: TestPoint; TestPoint_Keystone_5010-5014_Multipurpose; Digikey 36-5014-ND
C1: 10uF; C_0603_1608Metric; Digikey 478-8050-1-ND‎
D1: LED; D_0603_1608Metric; Digikey 475-3442-1-ND
GND1: TestPoint; TestPoint_Keystone_5010-5014_Multipurpose; Digikey 36-5014-ND
J1: LP-P10; PinHeader_1x03_P2.54mm_Vertical; Digikey A19430-ND
J2: LP-P7; PinHeader_2x05_P1.27mm_Vertical_SMD; Digikey SAM13165CT-ND
J3: Conn_01x08_Female; 8pin_1-27pitch_SMD; Digikey ED90570-ND
L1: 2.2uH; R_0805_2012Metric; Digikey 490-4994-1-ND‎
RXD1: TestPoint; TestPoint_Keystone_5010-5014_Multipurpose; Digikey 36-5014-ND
SW1: SW_SPDT; PinSocket_1x03_P2.54mm_Vertical; Digikey 360-2133-ND
TXD1: TestPoint; TestPoint_Keystone_5010-5014_Multipurpose; Digikey 36-5014-ND
U1: TPS62243_WSON; WSON-6-1EP_2x2mm_P0.65mm_EP1x1.6mm; Digikey 296-46476-1-ND‎

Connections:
+1V8: 1.8V1.1, C1.1, D1.1 (K), J2.1 (VTref), L1.2, U1.3 (FB)
+3V3: J1.1, J3.4, U1.4 (EN), U1.5 (VIN)
GND: C1.2, D1.2 (A), GND1.1, J2.3 (GND), J2.5 (GND), J2.9 (GNDDetect), J3.5, SW1.3 (C), U1.2 (MODE), U1.6 (GND)
JTAG_TCKC: J2.4 (SWDCLK/TCK), J3.3
JTAG_TMSC: J2.2 (SWDIO/TMS), J3.2
unnamed: J3.6, RXD1.1
unnamed: J3.7, TXD1.1
unnamed: J3.8, SW1.2 (B)
unnamed: L1.1, U1.1 (SW)
_RESET: J2.10 (~RESET~), J3.1

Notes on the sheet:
ET_VDD
LS_VDD
WMCU_VDD


Board: 2 copper layers, 28.0 x 30.0 mm, 12 parts (0 on the bottom side), 10 nets.

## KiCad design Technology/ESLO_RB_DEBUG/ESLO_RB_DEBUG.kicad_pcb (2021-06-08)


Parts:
BT1: Coin; BatteryHolder_Keystone_1058_1x2032; Digikey 36-1058-ND
C1, C2: 1uF; C_0402_1005Metric
D1: LED; D_0603_1608Metric
J1: LP-P10; PinHeader_1x03_P2.54mm_Vertical; Digikey A19430-ND
J2: LP-P7; PinHeader_2x05_P1.27mm_Vertical_SMD; Digikey SAM13165CT-ND
J3: ESLO-J2; ARBO_IO6_1.27mm
TP1, TP2: TestPoint; TestPoint_Keystone_5000-5004_Miniature; Digikey 36-5000-ND
U1: LP5907MFX-1.8; SOT-23-5; Digikey 296-41463-1-ND

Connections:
+1V8: C2.1, D1.1 (K), J1.2, J2.1 (VTref), TP1.1, U1.5 (OUT)
+3V3: J1.1, J3.1
GND: BT1.2 (-), C1.2, C2.2, D1.2 (A), J2.3 (GND), J2.5 (GND), J2.9 (GNDDetect), J3.2, J3.6, TP2.1, U1.2 (GND)
JTAG_TCKC: J2.4 (SWDCLK/TCK), J3.5
JTAG_TMSC: J2.2 (SWDIO/TMS), J3.4
unnamed: BT1.1 (+), C1.1, U1.1 (IN), U1.3 (EN)
_RESET: J2.10 (~RESET~), J3.3

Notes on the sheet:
ET_VDD
LS_VDD
WMCU_VDD
_DEBUG
Uses a coin cell to not interfere with EnergyTrace. *Coin cell does not power MCU
PWR GND


Board: 2 copper layers, 50.0 x 30.0 mm, 10 parts (0 on the bottom side), 7 nets.

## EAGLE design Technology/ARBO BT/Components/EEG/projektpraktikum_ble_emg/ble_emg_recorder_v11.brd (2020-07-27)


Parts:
C65: 100n; C0805; DIGIKEY 1276-1099-1-ND
C66: 1u; C0805; DIGIKEY 1276-1066-1-ND
LED1, LED2, LED3: LEDCHIPLED_0805; CHIPLED_0805
PCB1: PCB_DP_RECTANGLE-6.2X10; DP10062_V1
R41, R48: 10k; R0805
R49, R50, R51: 330; R0805; DIGIKEY RMCF0805JT330RCT-ND
S1: 31-XX; B3F-31XX
TEENSY: TEENSY_3.0_BASIC-SMD
U1: NRF8001-OLIMEX

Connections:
+3V3: C65.1, C66.1, R48.2, TEENSY.3.3V, TEENSY.3.3V1 (3.3V), U1.1 (3.3V); also elsewhere on the board
ADS_!CS: TEENSY.10; also elsewhere on the board
ADS_!DRDY: TEENSY.5; also elsewhere on the board
ADS_!PWDN: TEENSY.2; also elsewhere on the board
ADS_!RESET: TEENSY.3; also elsewhere on the board
ADS_START: TEENSY.4; also elsewhere on the board
GND: C65.2, C66.2, R41.1, R49.1, R50.1, R51.1, S1.1, TEENSY.AGND, TEENSY.GND, TEENSY.GND1 (GND), U1.2 (GND); also elsewhere on the board
MISO: TEENSY.12, U1.9 (MISO); also elsewhere on the board
MOSI: TEENSY.11, U1.8 (MOSI); also elsewhere on the board
unnamed: R48.1, S1.2 (S), TEENSY.15/A1
unnamed: LED1.A, TEENSY.16/A2
unnamed: LED2.A, TEENSY.17/A3
unnamed: LED3.A, TEENSY.18/A4
unnamed: LED1.C, R49.2
unnamed: LED2.C, R50.2
unnamed: LED3.C, R51.2
NRF_!RESET: R41.2, TEENSY.7, U1.3 (!RST)
NRF_RDYN: TEENSY.8, U1.10 (RDYN)
NRF_REQN: TEENSY.9, U1.7 (REQN)
PSU_NEG: TEENSY.1; also elsewhere on the board
PSU_POS: TEENSY.0; also elsewhere on the board
SCK: TEENSY.13, U1.6 (SCK); also elsewhere on the board
VBAT: TEENSY.VIN; also elsewhere on the board

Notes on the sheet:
ADS ctrl signals
NRF ctrl signals
SPI
BLE connected EMG recorder
MCU and BLE module


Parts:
BATCON: JST_2PIN-THM-RA; JST-PH-2-THM-RA; DIGIKEY 455-1719-ND
C37, C38, C39, C41, C42, C44: 10u; C0805; DIGIKEY 1276-2891-1-ND
C40, C43: 10n; C0805; DIGIKEY 1276-1015-1-ND
C45: 100n; C0805; DIGIKEY 1276-1099-1-ND
C46, C47, C48, C67: 1u; C0805; DIGIKEY 1276-1066-1-ND
CN1: USBMINIB; USB-MINIB; DIGIKEY ED2992CT-ND
Q1, Q2: CSD16406Q3; DQV8-L; DIGIKEY 296-24251-1-ND
R36: 2.2k; R0805; DIGIKEY RMCF0805JT2K20CT-ND
R37: 330; R0805; DIGIKEY RMCF0805JT330RCT-ND
R42, R43, R44, R45: DNP; R0805
R46, R47: 10k; R0805
U3: LM2664M6; SOT95P300X120-6N; DIGIKEY LM2664M6CT-ND
U4: TPS72301DBV; DBV5; DIGIKEY 296-15799-1-ND
U5: TPS73201DBV; DBV5; DIGIKEY 296-15810-1-ND
U6: BQ24380DSG; DSG8_P9X1P6; DIGIKEY 296-23385-1-ND
U7: BQ29700DSE; DSE6; DIGIKEY 296-37746-1-ND
U8: MCP73811/2; SOT23-5L; DIGIKEY MCP73811T-420I/OTCT-ND

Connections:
+2V5: C44.1, R42.1, U5.5 (OUT); also elsewhere on the board
-2V5: C41.1, R45.1, U4.5 (OUT); also elsewhere on the board
GND: C38.2, C39.2, C40.2, C41.2, C42.2, C43.2, C44.2, C46.2, C47.2, C48.2, C67.2, CN1.GND, Q2.1 (S), Q2.2 (S), Q2.3 (S), R36.1, R43.2, R44.2, R46.1, R47.1, U3.1 (GND), U4.1 (GND), U5.2 (GND), U6.2 (VSS), U6.5 (!CE), U6.6 (VBAT), U6.9 (EPAD), U8.2 (VSS); also elsewhere on the board
unnamed: C40.1, R44.1, R45.2, U4.4 (FB/NR)
unnamed: C46.1, C47.1, U6.8 (OUT), U8.1 (CE), U8.4 (VDD), U8.5 (PROG)
unnamed: C37.1, U3.6 (CAP+)
unnamed: C37.2, U3.3 (CAP-)
unnamed: C39.1, U3.2 (OUT), U4.2 (IN)
unnamed: C43.1, R42.2, R43.1, U5.4 (NR/FB)
unnamed: BATCON.2 (1), C45.2, Q1.1 (S), Q1.2 (S), Q1.3 (S), U7.4 (VSS)
unnamed: Q2.4 (G), U7.2 (COUT)
unnamed: Q1.4 (G), U7.3 (DOUT)
unnamed: R36.2, U7.6 (V-)
unnamed: C45.1, R37.2, U7.5 (BAT)
unnamed: Q1.5 (D), Q1.6 (D), Q1.7 (D), Q1.8 (D), Q2.5 (D), Q2.6 (D), Q2.7 (D), Q2.8 (D)
PSU_NEG: R47.2, U3.4 (!SD), U4.3 (EN); also elsewhere on the board
PSU_POS: R46.2, U5.3 (!EN); also elsewhere on the board
VAC: C48.1, CN1.VBUS, U6.1 (IN)
VBAT: BATCON.1 (2), C38.1, C42.1, C67.1, R37.1, U3.5 (V+), U5.1 (IN), U8.3 (VBAT); also elsewhere on the board

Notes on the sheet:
-3.7V
BLE connected EMG recorder
Power supply


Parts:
C1, C2, C3, C4, C5, C6, C7, C8, C9, C10, C11, C12, C13, C14, C15, C16, C17, C18, C19, C20, C21, C22, C23, C24, C25, C26, C27, C28, C29, C30, C31, C32, C34, C35: 270p; C0805; DIGIKEY 1276-2494-1-ND
C33: 1.5n; C0805; DIGIKEY 1276-1794-1-ND
C36: 100n; C0805; DIGIKEY 1276-1099-1-ND
C49, C55, C58, C59, C61, C70: 1u; C0805; DIGIKEY 1276-1066-1-ND
C50, C51, C52, C53, C54, C56, C57, C63, C68, C69: 100n; C0402; DIGIKEY 1276-1443-1-ND
C60: 100u; D/7343-31W; DIGIKEY 399-3772-1-ND
C62: 10u; C0805; DIGIKEY 1276-2891-1-ND
C64: 1n; C0402; DIGIKEY 311-1036-1-ND
D1, D2, D3, D4, D5, D6, D7, D8, D9, D10, D11, D12, D13, D14, D15, D16, D17: MMBZAL5V6; SOT23; DIGIKEY 568-6347-1-ND
JP1: JP1E; JP1
L1, L2: MH2029; L0805; DIGIKEY MH2029-221YCT-ND
R1, R2, R3, R4, R5, R6, R7, R8, R9, R10, R11, R12, R13, R14, R15, R16, R17, R18, R19, R20, R21, R22, R23, R24, R25, R26, R27, R28, R29, R30, R31, R32, R34, R35: 2.61k; R0805; DIGIKEY RMCF0805FT2K61CT-ND
R33: 1M; R0805; DIGIKEY RMCF0805JT1M00CT-ND
R38, R39, R40: 10k; R0805
SV1: MA05-2
SV2: ML40; DIGIKEY S9175-ND
U2: ADS1298PAG; PAG64; DIGIKEY 296-27734-ND
X1: CB3LV; SM77H; DIGIKEY CTX1277CT-ND

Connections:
+2V5: L1.2; also elsewhere on the board
+3V3: C36.1, C68.1, C69.1, C70.1, R38.2, U2.48 (DVDD), U2.50 (DVDD), X1.4 (VCC); also elsewhere on the board
-2V5: L2.1; also elsewhere on the board
ABIAS: D17.2, R34.1, SV2.38
ADS_!CS: U2.39 (!CS); also elsewhere on the board
ADS_!DRDY: U2.47 (!DRDY); also elsewhere on the board
ADS_!PWDN: R39.2, U2.35 (!PWDN); also elsewhere on the board
ADS_!RESET: R40.2, U2.36 (!RESET); also elsewhere on the board
ADS_CLK: U2.37 (CLK), X1.3 (OUT)
ADS_START: U2.38 (START); also elsewhere on the board
AINN1: D9.2, R17.1, SV2.4
AINN2: D10.2, R19.1, SV2.8
AINN3: D11.2, R21.1, SV2.12
AINN4: D12.2, R23.1, SV2.16
AINN5: D13.2, R25.1, SV2.20
AINN6: D14.2, R27.1, SV2.24
AINN7: D15.2, R29.1, SV2.28
AINN8: D16.2, R31.1, SV2.32
AINP1: D1.2, R1.1, SV2.3
AINP2: D2.2, R3.1, SV2.7
AINP3: D3.2, R5.1, SV2.11
AINP4: D4.2, R7.1, SV2.15
AINP5: D5.2, R9.1, SV2.19
AINP6: D6.2, R11.1, SV2.23
AINP7: D7.2, R13.1, SV2.27
AINP8: D8.2, R15.1, SV2.31
BIASOUT: C35.2, R35.2, SV1.5, SV1.7, SV1.9, U2.63 (RLDOUT)
GND: C1.1, C2.1, C3.1, C4.1, C5.1, C6.1, C7.1, C8.1, C9.1, C10.1, C11.1, C12.1, C13.1, C14.1, C15.1, C16.1, C17.1, C18.1, C19.1, C20.1, C21.1, C22.1, C23.1, C24.1, C25.1, C26.1, C27.1, C28.1, C29.1, C30.1, C31.1, C32.1, C34.1, C35.1, C36.2, C68.2, C69.2, C70.2, D1.1, D2.1, D3.1, D4.1, D5.1, D6.1, D7.1, D8.1, D9.1, D10.1, D11.1, D12.1, D13.1, D14.1, D15.1, D16.1, D17.1, JP1.2, R39.1, R40.1, SV2.1, SV2.2, SV2.5, SV2.6, SV2.9, SV2.10, SV2.13, SV2.14, SV2.17, SV2.18, SV2.21, SV2.22, SV2.25, SV2.26, SV2.29, SV2.30, SV2.33, SV2.34, SV2.35, SV2.36, SV2.37, SV2.39, SV2.40, U2.31 (RESV1), U2.33 (DGND), U2.49 (DGND), U2.51 (DGND), X1.2 (GND); also elsewhere on the board
INN1: C18.2, R18.2, U2.15 (IN1N)
INN2: C20.2, R20.2, U2.13 (IN2N)
INN3: C22.2, R22.2, U2.11 (IN3N)
INN4: C24.2, R24.2, U2.9 (IN4N)
INN5: C26.2, R26.2, U2.7 (IN5N)
INN6: C28.2, R28.2, U2.5 (IN6N)
INN7: C30.2, R30.2, U2.3 (IN7N)
INN8: C32.2, R32.2, U2.1 (IN8N)
INP1: C2.2, R2.2, U2.16 (IN1P)
INP2: C4.2, R4.2, U2.14 (IN2P)
INP3: C6.2, R6.2, U2.12 (IN3P)
INP4: C8.2, R8.2, U2.10 (IN4P)
INP5: C10.2, R10.2, U2.8 (IN5P)
INP6: C12.2, R12.2, U2.6 (IN6P)
INP7: C14.2, R14.2, U2.4 (IN7P)
INP8: C16.2, R16.2, U2.2 (IN8P)
MISO: U2.43 (DOUT); also elsewhere on the board
MOSI: U2.34 (DIN); also elsewhere on the board
unnamed: C1.2, R1.2, R2.1
unnamed: C3.2, R3.2, R4.1
unnamed: C34.2, R34.2, R35.1
unnamed: C5.2, R5.2, R6.1
unnamed: C7.2, R7.2, R8.1
unnamed: SV1.6, SV1.10, U2.62 (RLDIN)
unnamed: C9.2, R9.2, R10.1
unnamed: C33.2, R33.1, SV1.8
unnamed: C11.2, R11.2, R12.1
unnamed: C33.1, R33.2, SV1.4, U2.61 (RLDINV)
unnamed: C13.2, R13.2, R14.1
unnamed: C15.2, R15.2, R16.1
unnamed: SV1.2, U2.60 (RLDREF)
unnamed: C17.2, R17.2, R18.1
unnamed: C19.2, R19.2, R20.1
unnamed: C21.2, R21.2, R22.1
unnamed: C23.2, R23.2, R24.1
unnamed: C25.2, R25.2, R26.1
unnamed: C27.2, R27.2, R28.1
unnamed: C29.2, R29.2, R30.1
unnamed: C31.2, R31.2, R32.1
unnamed: JP1.1, R38.1, U2.52 (CLKSEL)
unnamed: C64.1, U2.64 (WCT)
SCK: U2.40 (SCLK); also elsewhere on the board
SRB1: SV1.1, U2.17 (TESTP_PACE_OUT1)
SRB2: SV1.3, U2.18 (TESTN_PACE_OUT2)
V+: C49.1, C50.1, C51.1, C52.1, C53.1, C54.1, C55.1, C56.1, L1.1, U2.19 (AVDD), U2.21 (AVDD), U2.22 (AVDD), U2.54 (AVDD1), U2.56 (AVDD), U2.59 (AVDD)
V-: C49.2, C50.2, C51.2, C52.2, C53.2, C54.2, C55.2, C56.2, C57.2, C58.2, C59.2, C60.-, C61.2, C62.2, C63.2, C64.2, L2.2, U2.20 (AVSS), U2.23 (AVSS), U2.25 (VREFN), U2.32 (AVSS), U2.53 (AVSS1), U2.57 (AVSS), U2.58 (AVSS)
VCAP1: C60.+, U2.28 (VCAP1)
VCAP2: C59.1, U2.30 (VCAP2)
VCAP3: C57.1, C58.1, U2.55 (VCAP3)
VCAP4: C61.1, U2.26 (VCAP4)
VREFP: C62.1, C63.1, U2.24 (VREFP)

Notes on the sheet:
AVDD decoupling
AVDD1 decoupling
BLE connected EMG recorder
ADS1298 Analog Front End
DVDD decoupling



Board: 8 copper layers, 100.0 x 62.0 mm, 163 parts (18 on the bottom side), 105 nets.

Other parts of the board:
U$5: KOM_LOGO

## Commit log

2019-12-05 Including Testbed design
    [ARBO Testbed.kicad_pcb, ARBO Testbed.sch, ARBO Testbed_bom_.csv, ARBO Testbed_bom_.xlsx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]
2019-12-05 Including KiCad
    [Coilcraft-PA6512-AE.step, QFN-24 3x3 0.4mm.ipt, QFN-24 3x3 0.4mm.stp]
2019-12-14 Wiki QR code
    [ARBO Testbed.kicad_pcb]
2019-12-21 Updated testbed
    [ARBO Testbed.kicad_pcb, ARBO Testbed_bom_.xlsx]
2020-01-06 Updating values to match changes on board
    [ARBO Testbed.kicad_pcb, ARBO Testbed.sch]
2020-01-07 ARBO Mini hackathon
    [ARBO Mini.dsn, ARBO Mini.kicad_pcb, ARBO Mini.sch]
2020-01-08 Exported gerbers
    [ARBO Mini-B_Cu.gbr, ARBO Mini-B_Mask.gbr, ARBO Mini-B_SilkS.gbr, ARBO Mini-Edge_Cuts.gbr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]
2020-01-09 ARBO mini sent to JSTPCB for fab
    [ARBO Mini-B_Cu.gbr, ARBO Mini-B_Mask.gbr, ARBO Mini-B_SilkS.gbr, ARBO Mini-Edge_Cuts.gbr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]
2020-01-23 ARBO mini FRAM pads are backwards, fix later
    [ARBO Mini.kicad_pcb, ARBO Mini.sch]
2020-03-04 Changing RF design for BT
    [ARBO Mini.kicad_pcb]
2020-04-01 Added ARBO BT and NUTS
    [ARBO BT-B_Cu.gbr, ARBO BT-B_Mask.gbr, ARBO BT-B_Paste.gbr, ARBO BT-B_SilkS.gbr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]
2020-04-03 Got Nuts PCB prototype working, needs updates
    [NUTS_PCB.sch]
2020-07-27 Working on pink noise
    [NUTS_PCB.sch, ble_emg_recorder_v11-bom.ods, ble_emg_recorder_v11.GBL, ble_emg_recorder_v11.GBO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]
2020-08-18 Added ESLO
    [ESLO.kicad_pcb, ESLO.sch]
2020-08-21 ESLO changelog
    [ESLO.kicad_pcb, ESLO.sch, ZXG0064A.stp]
2020-08-25 Added ESLO debugger and PSP
    [ESLO-B_Cu.gbr, ESLO-B_Mask.gbr, ESLO-B_Paste.gbr, ESLO-B_SilkS.gbr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]
2020-08-28 ESLO project updates
    [ESLO-B_Cu.gbr, ESLO-B_Mask.gbr, ESLO-B_Paste.gbr, ESLO-B_SilkS.gbr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]
2020-09-02 Reconsidering ESLO architecture (-> CC2640R2)
    [ESLO.sch, ESLO_Debugger.sch, ESLO_PSP.kicad_pcb, ESLO_PSP.sch]
2020-09-18 ESLO RB
    [CC2650EM-4XS-Ext-Reg_2_0_0_BOM.xlsx, CC2650EM-JohBal_2_0_0_BOM.xlsx, CC26XX_4X4_EXT_REG.DSN, CC26xx_4x4_Ext_Reg_lvl_shifter.brd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]
2020-09-23 Redo ESLO_RB with AC coupling
    [ESLO_RB.kicad_pcb, ESLO_RB.sch, MCU067B.DSN, MCU067B_BOM.xlsx]
2020-09-24 Completed RB design
    [ESLO_RB.kicad_pcb, ESLO_RB.sch]
2020-09-24 Checked all pins, ready for production
    [ESLO_RB-B_Cu.gbr, ESLO_RB-B_Mask.gbr, ESLO_RB-B_Paste.gbr, ESLO_RB-B_SilkS.gbr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]
2020-09-28 Submit ESLO_RB for mfg w PCBONLINE
    [2020-09-27T094132.csv, CC2650EM-4XS-Ext-Reg_2_0_0_BOM.xlsx, CC2650EM-JohBal_2_0_0_BOM.xlsx, CC26XX_4X4_EXT_REG.DSN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]
2020-10-04 Debugger submitted
    [ESLO_RB.kicad_pcb, ESLO_RB.sch]
2020-10-21 Assembling ESLO_RB
    [ESLO_RB.kicad_pcb, ESLO_RB.sch]
2020-10-27 ESLO Updates
    [ESLO_RB.kicad_pcb, ESLO_RB.sch]
2020-10-31 Debugging ESLO PBCs
    [ESLO_RB.kicad_pcb, ESLO_RB.sch]
2020-11-10 Submitted ESLO_RB for TI hardware review
    [ESLO_RB_bom_.csv]
2021-01-19 NAND updates
    [ESLO_RB.kicad_pcb]
2021-02-17 Updated note on ESLO_RB
    [ESLO_RB.kicad_pcb, ESLO_RB.sch]
2021-05-14 ESLO RB2
    [CC2650EM-4XS-Ext-Reg_2_0_0_BOM.xlsx, CC26XX_4X4_EXT_REG.DSN, CC26xx_4x4_Ext_Reg_lvl_shifter.brd, ESLO_RB.kicad_pcb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]
2021-06-08 Adding all schematics/layouts/tech projects
    [473093351.stp, ANT7-T-24LR-MB1254-A.GBL, ANT7-T-24LR-MB1254-A.GBO, ANT7-T-24LR-MB1254-A.GBS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]
2021-07-28 Update schematics
    [ESLO_RB2.kicad_pcb, ESLO_RB2.sch, ESLO_RB2_DataDump.sch]
